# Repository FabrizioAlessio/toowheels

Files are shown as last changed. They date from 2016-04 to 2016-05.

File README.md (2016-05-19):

# toowheels
TooWheels is a DIY wheelchair for people with disability. I'ts a patent pending project of Fabrizio Alessio, released in open source version (CC licence non commercial,share alike international 4.0) to be usefull for people all over the world.

For any information see our website www.toowheels.org, our Facebook page "toowheels" or feel free to contact by mail at: alessiofabriziogiorgio@gmail.com

I'ts an evolving project of Fabrizio Alessio started in FabLabTorino, selected in 2014 as one of the 30 best project in the world at the "Global Fab Awards" and winner of the italian prize "Compasso d'Oro - Targa Giovani" at the XXIV edition of the ADI DESIGN INDEX. 

We are developing a lots of projects all around the world, involving FabLabs, Associations, Designers and Research groups. Contact us and join TooWheels project!

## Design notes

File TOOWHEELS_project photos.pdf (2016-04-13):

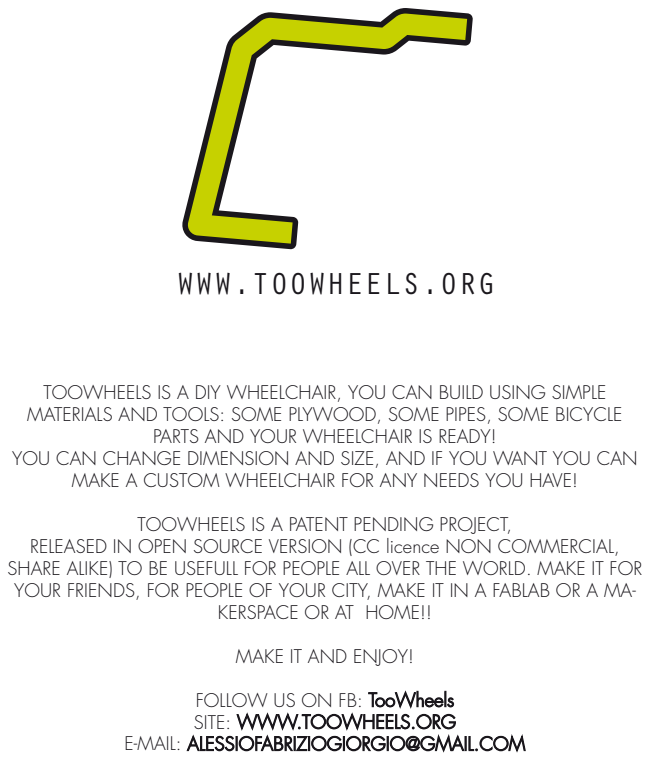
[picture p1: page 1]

WWW.TOOWHEELS.ORG

TOOWHEELS IS A DIY WHEELCHAIR, YOU CAN BUILD USING SIMPLE
MATERIALS AND TOOLS: SOME PLYWOOD, SOME PIPES, SOME BICYCLE
YOU CAN CHANGE DIMENSION AND SIZE, AND IF YOU WANT YOU CAN
MAKE A CUSTOM WHEELCHAIR FOR ANY NEEDS YOU HAVE!
TOOWHEELS IS A PATENT PENDING PROJECT,

PARTS AND YOUR WHEELCHAIR IS READY!

RELEASED IN OPEN SOURCE VERSION (CC licence NON COMMERCIAL,
SHARE ALIKE) TO BE USEFULL FOR PEOPLE ALL OVER THE WORLD. MAKE IT FOR
YOUR FRIENDS, FOR PEOPLE OF YOUR CITY, MAKE IT IN A FABLAB OR A MA-

KERSPACE OR AT HOME!!
MAKE IT AND ENJOY!
FOLLOW US ON FB: TooWheels
SITE: WWW.TOOWHEELS.ORG
E-MAIL: ALESSIOFABRIZIOGIORGIO@GMAIL.COM

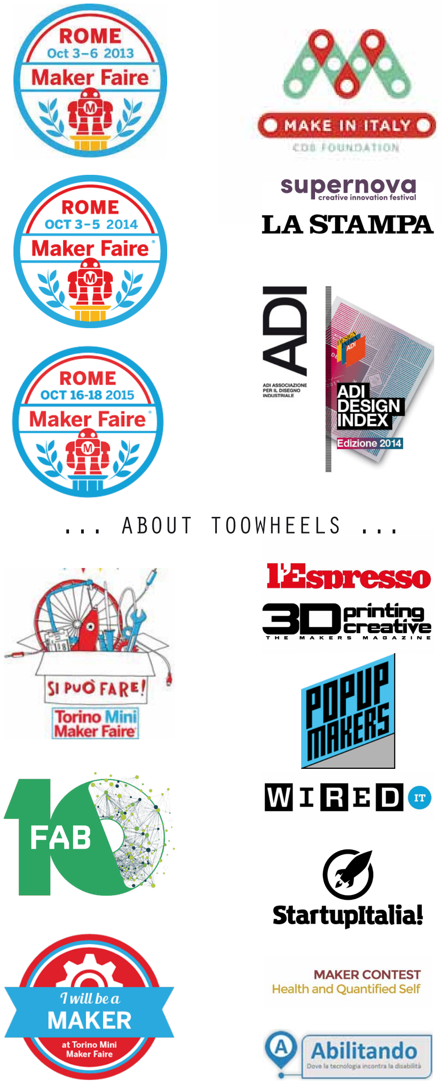
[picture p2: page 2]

... ABOUT TOOWHEELS ...

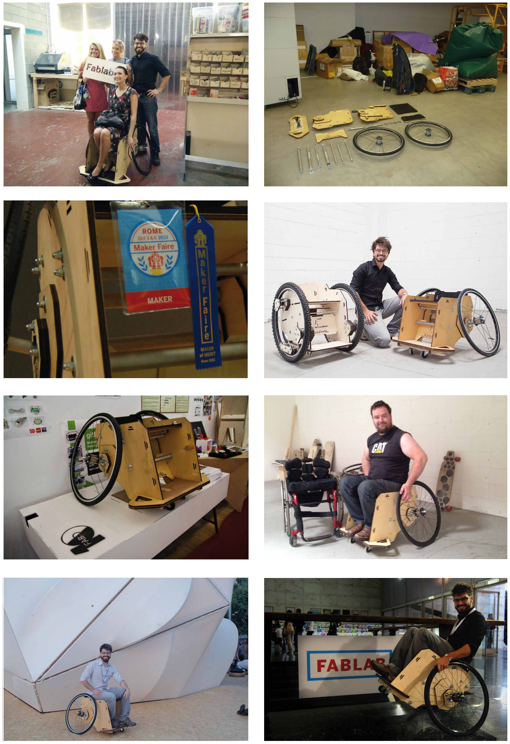
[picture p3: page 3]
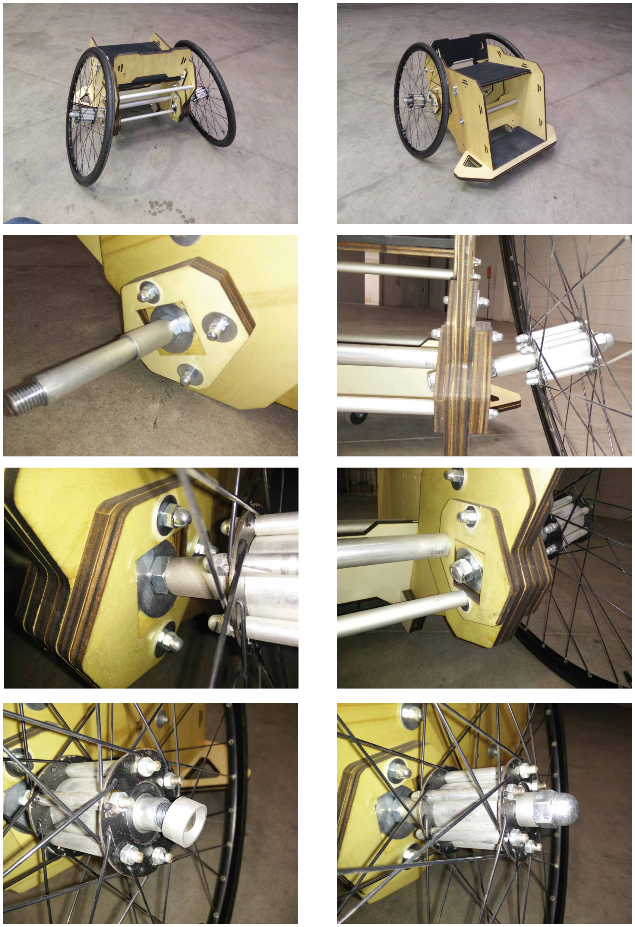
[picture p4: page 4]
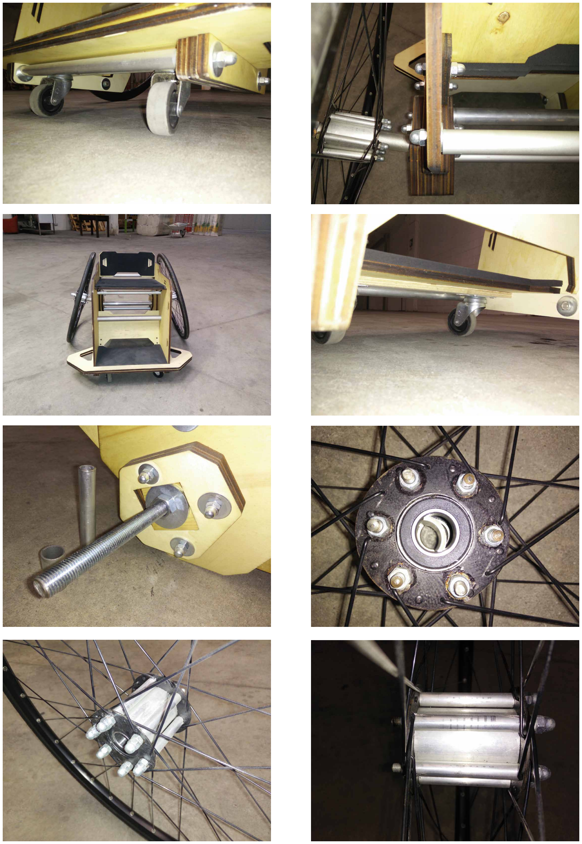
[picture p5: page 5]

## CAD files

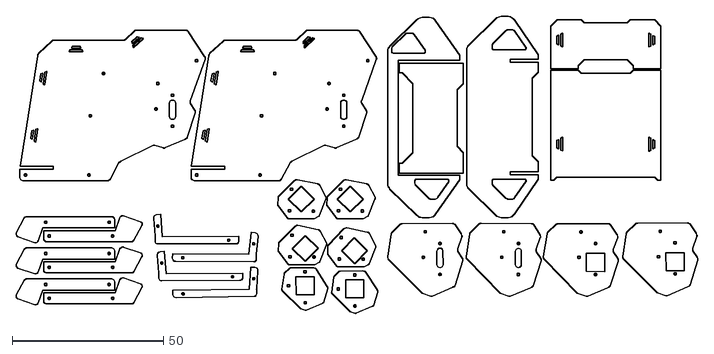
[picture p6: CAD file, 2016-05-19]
TOOWHEELS_2D PLANS.dxf
225.4 x 98.2

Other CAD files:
TOOWHEELS_2D PLANS.dwg

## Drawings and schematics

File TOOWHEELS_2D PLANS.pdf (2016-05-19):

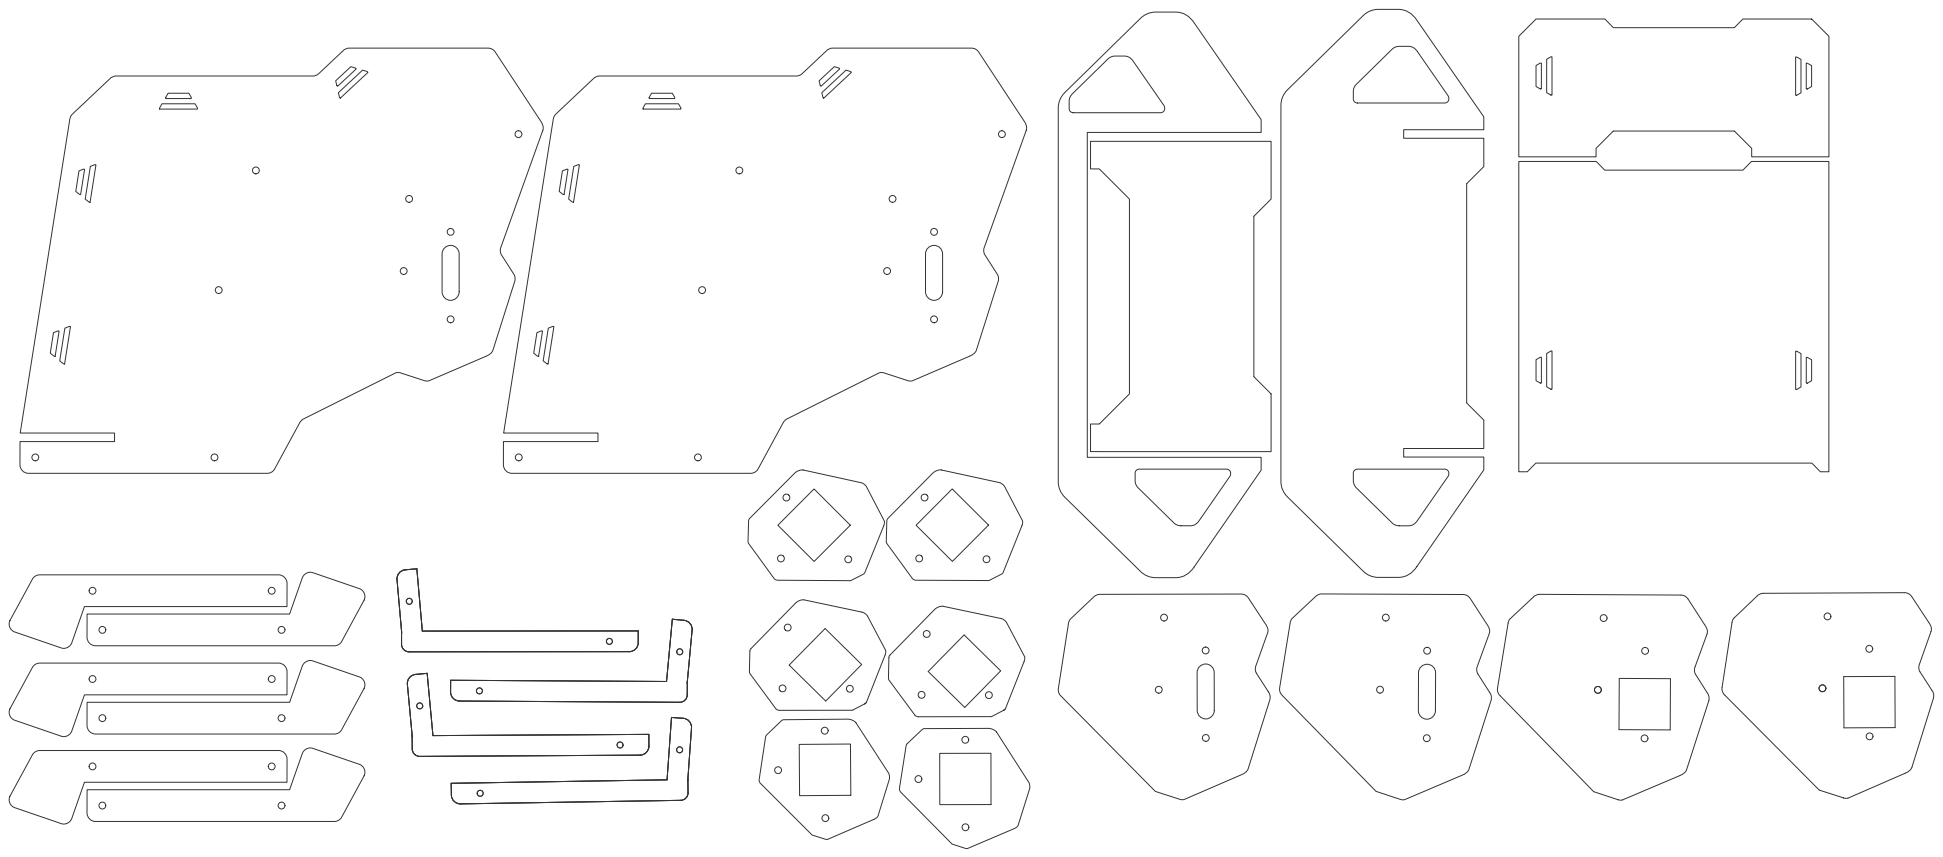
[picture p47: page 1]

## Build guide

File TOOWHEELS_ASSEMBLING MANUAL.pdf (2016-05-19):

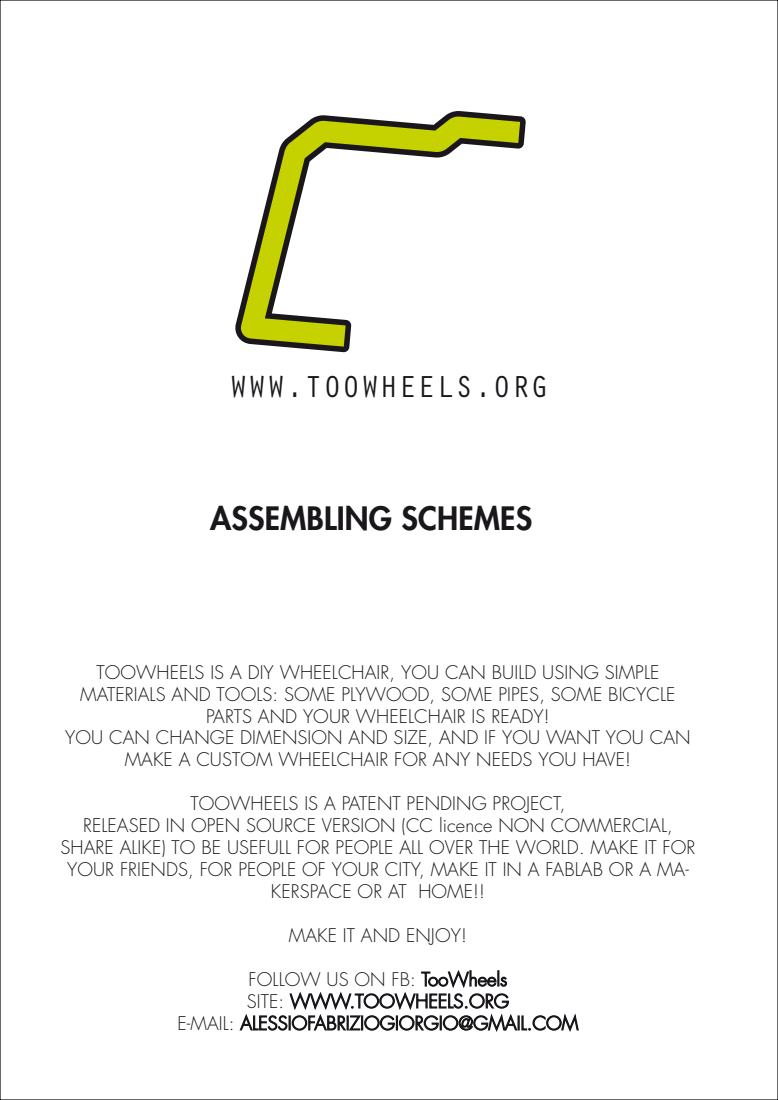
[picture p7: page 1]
ASSEMBLING SCHEMES

WWW.TOOWHEELS.ORG

TOOWHEELS IS A DIY WHEELCHAIR, YOU CAN BUILD USING SIMPLE
MATERIALS AND TOOLS: SOME PLYWOOD, SOME PIPES, SOME BICYCLE
YOU CAN CHANGE DIMENSION AND SIZE, AND IF YOU WANT YOU CAN
MAKE A CUSTOM WHEELCHAIR FOR ANY NEEDS YOU HAVE!
TOOWHEELS IS A PATENT PENDING PROJECT,

PARTS AND YOUR WHEELCHAIR IS READY!

RELEASED IN OPEN SOURCE VERSION (CC licence NON COMMERCIAL,
SHARE ALIKE) TO BE USEFULL FOR PEOPLE ALL OVER THE WORLD. MAKE IT FOR
YOUR FRIENDS, FOR PEOPLE OF YOUR CITY, MAKE IT IN A FABLAB OR A MA-

KERSPACE OR AT HOME!!
MAKE IT AND ENJOY!
FOLLOW US ON FB: TooWheels
SITE: WWW.TOOWHEELS.ORG
E-MAIL: ALESSIOFABRIZIOGIORGIO@GMAIL.COM

## POSIZIONA LA SEDUTA

1

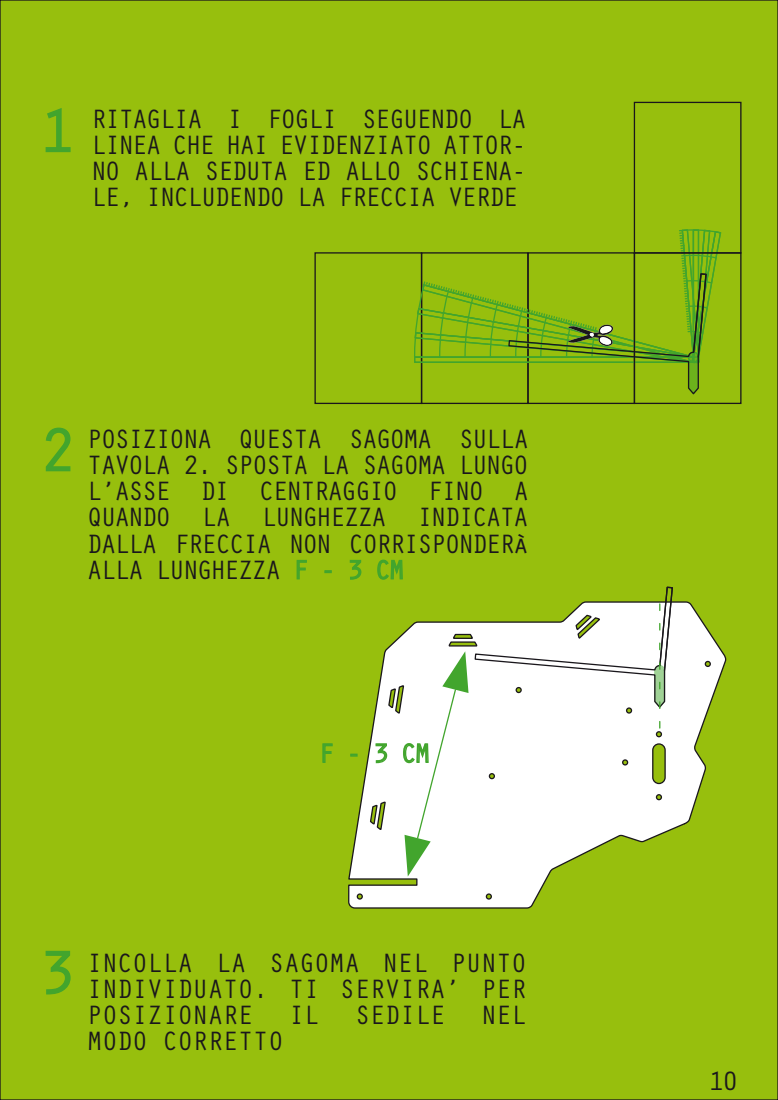
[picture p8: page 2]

RITAGLIA I FOGLI SEGUENDO LA
LINEA CHE HAI EVIDENZIATO ATTOR- NO ALLA SEDUTA ED ALLO SCHIENA- LE, INCLUDENDO LA FRECCIA VERDE

POSIZIONA QUESTA SAGOMA SULLA
TAVOLA 2. SPOSTA LA SAGOMA LUNGO
L’ASSE DI CENTRAGGIO FINO A
QUANDO LA LUNGHEZZA INDICATA
DALLA FRECCIA NON CORRISPONDERà
ALLA LUNGHEZZA F - 3 CM

INCOLLA LA SAGOMA NEL PUNTO
INDIVIDUATO. TI SERVIRA’ PER
POSIZIONARE IL SEDILE NEL
MODO CORRETTO

## BACKREST,SEAT,BUMPER SUPPORT

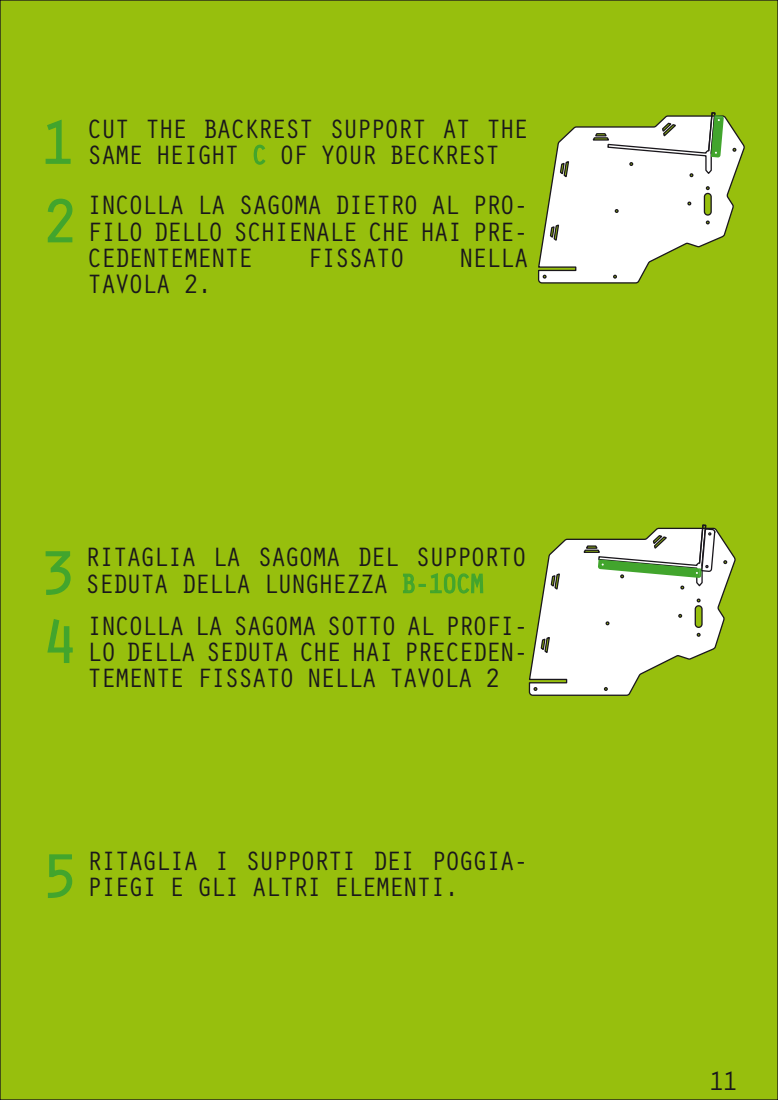
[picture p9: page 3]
2INCOLLA LA SAGOMA DIETRO AL PRO- FILO DELLO SCHIENALE CHE HAI PRE- CEDENTEMENTE; FISSATO; NELLA; TAVOLA 2.

1 CUT THE BACKREST SUPPORT AT THE
SAME HEIGHT C OF YOUR BECKREST

3RITAGLIA LA SAGOMA DEL SUPPORTO
SEDUTA DELLA LUNGHEZZA B-10CM
4INCOLLA LA SAGOMA SOTTO AL PROFI- LO DELLA SEDUTA CHE HAI PRECEDEN- TEMENTE FISSATO NELLA TAVOLA 2

5RITAGLIA I SUPPORTI DEI POGGIA- PIEGI E GLI ALTRI ELEMENTI.

ASSEMBLAGGIO | FASE11

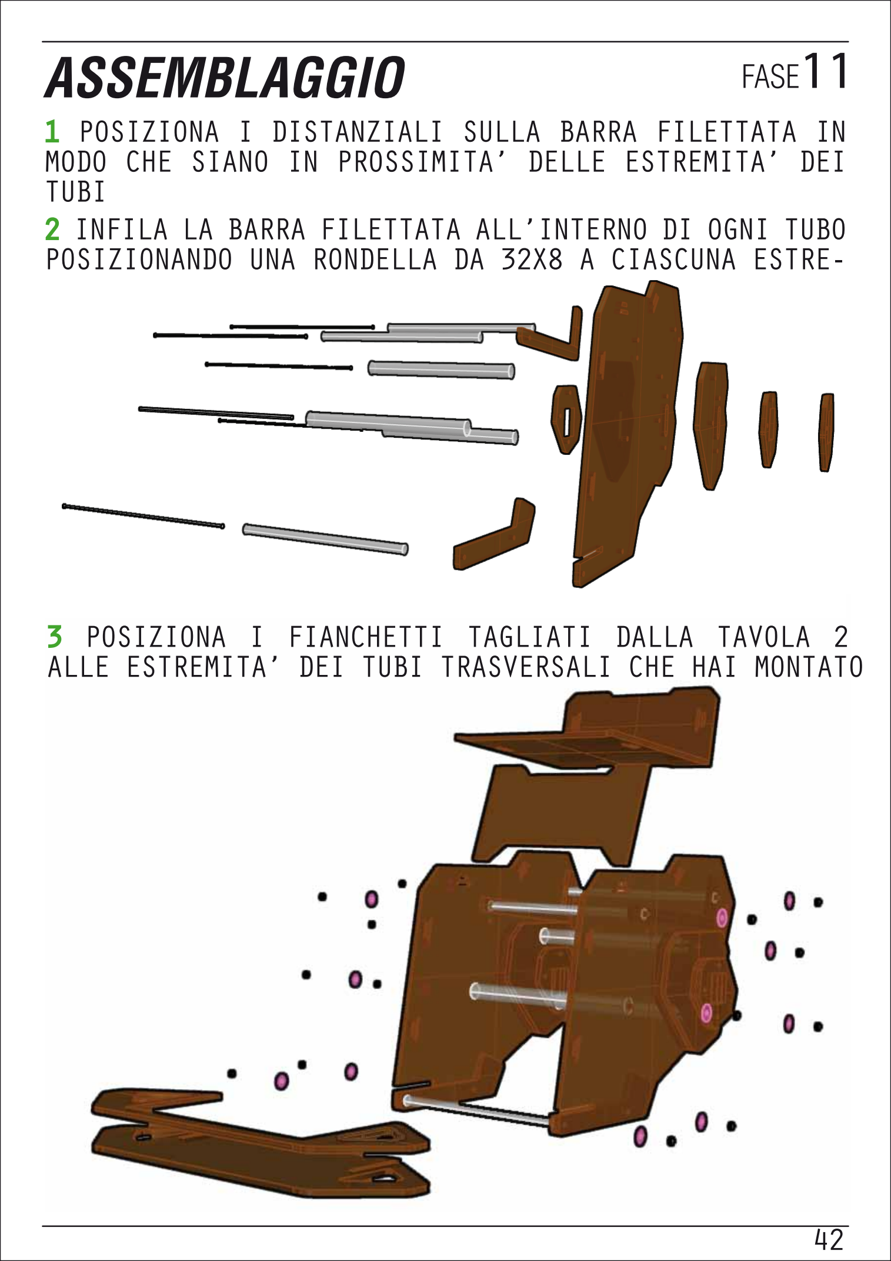
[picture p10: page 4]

1 POSIZIONA I DISTANZIALI SULLA BARRA FILETTATA IN MODO CHE SIANO IN PROSSIMITA’ DELLE ESTREMITA’ DEI TUBI
2 INFILA LA BARRA FILETTATA ALL’INTERNO DI OGNI TUBO POSIZIONANDO UNA RONDELLA DA 32X8 A CIASCUNA ESTRE- MITA’

3 POSIZIONA I FIANCHETTI TAGLIATI DALLA TAVOLA 2 ALLE ESTREMITA’ DEI TUBI TRASVERSALI CHE HAI MONTATO

## PIPES AND RODS

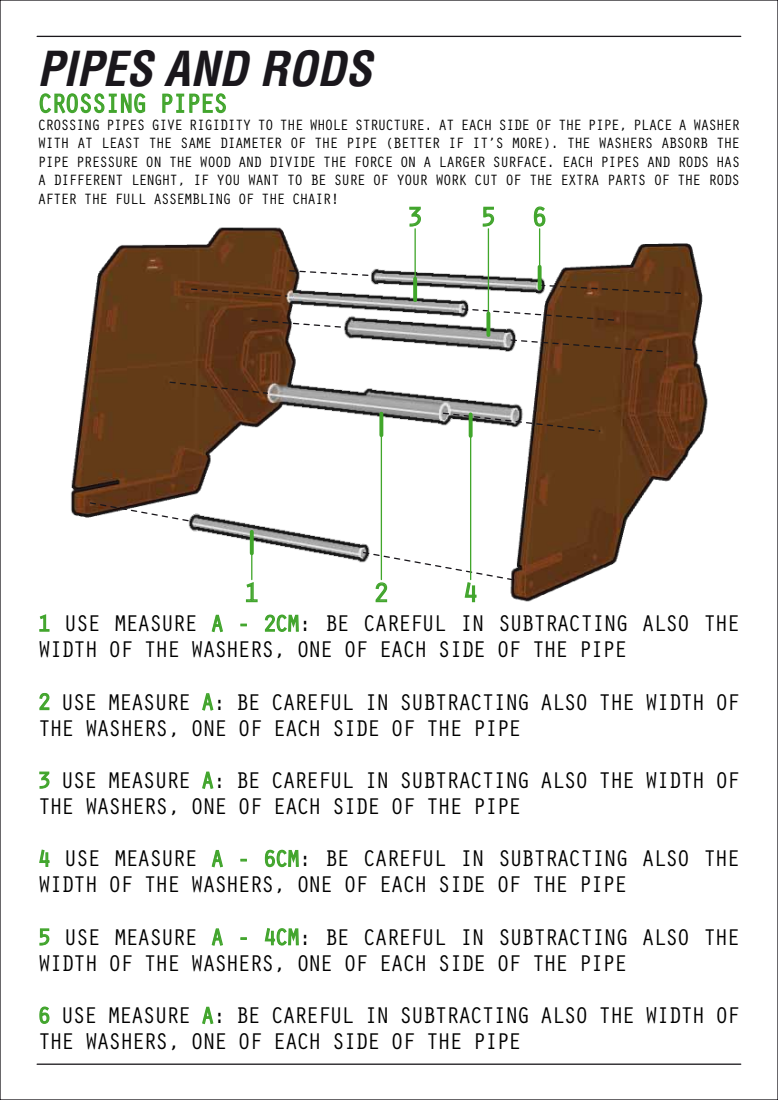
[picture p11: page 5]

CROSSING PIPES
CROSSING PIPES GIVE RIGIDITY TO THE WHOLE STRUCTURE. AT EACH SIDE OF THE PIPE, PLACE A WASHER
WITH AT LEAST THE SAME DIAMETER OF THE PIPE (BETTER IF IT’S MORE). THE WASHERS ABSORB THE
PIPE PRESSURE ON THE WOOD AND DIVIDE THE FORCE ON A LARGER SURFACE. EACH PIPES AND RODS HAS
A DIFFERENT LENGHT, IF YOU WANT TO BE SURE OF YOUR WORK CUT OF THE EXTRA PARTS OF THE RODS
AFTER THE FULL ASSEMBLING OF THE CHAIR!

1 USE MEASURE A - 2CM: BE CAREFUL IN SUBTRACTING ALSO THE
WIDTH OF THE WASHERS, ONE OF EACH SIDE OF THE PIPE
2 USE MEASURE A: BE CAREFUL IN SUBTRACTING ALSO THE WIDTH OF
THE WASHERS, ONE OF EACH SIDE OF THE PIPE
3 USE MEASURE A: BE CAREFUL IN SUBTRACTING ALSO THE WIDTH OF
4 USE MEASURE A - 6CM: BE CAREFUL IN SUBTRACTING ALSO THE
5 USE MEASURE A - 4CM: BE CAREFUL IN SUBTRACTING ALSO THE
6 USE MEASURE A: BE CAREFUL IN SUBTRACTING ALSO THE WIDTH OF

## HUB

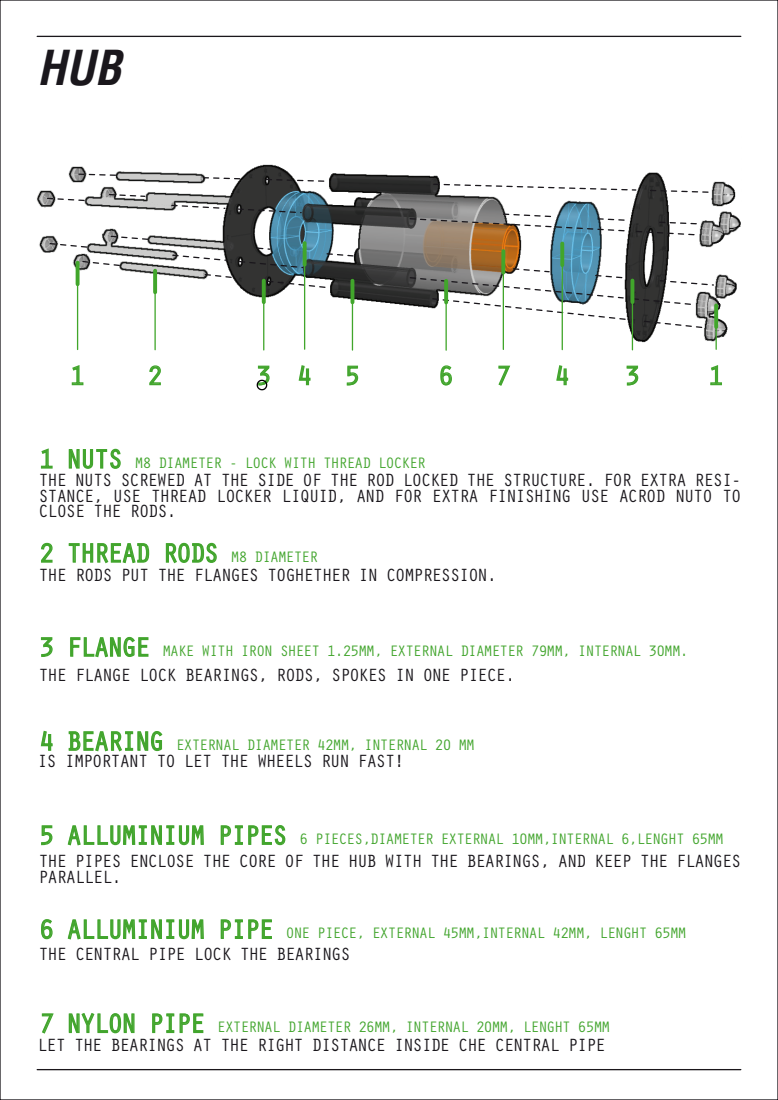
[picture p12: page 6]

1 NUTS M8 DIAMETER - LOCK WITH THREAD LOCKER
THE NUTS SCREWED AT THE SIDE OF THE ROD LOCKED THE STRUCTURE. FOR EXTRA RESI- STANCE, USE THREAD LOCKER LIQUID, AND FOR EXTRA FINISHING USE ACROD NUTO TO
CLOSE THE RODS.
2 THREAD RODS M8 DIAMETER
THE RODS PUT THE FLANGES TOGHETHER IN COMPRESSION.

3 FLANGE MAKE WITH IRON SHEET 1.25MM, EXTERNAL DIAMETER 79MM, INTERNAL 30MM.
THE FLANGE LOCK BEARINGS, RODS, SPOKES IN ONE PIECE.

4 BEARING EXTERNAL DIAMETER 42MM, INTERNAL 20 MM
IS IMPORTANT TO LET THE WHEELS RUN FAST!

5 ALLUMINIUM PIPES 6 PIECES,DIAMETER EXTERNAL 10MM,INTERNAL 6,LENGHT 65MM
THE PIPES ENCLOSE THE CORE OF THE HUB WITH THE BEARINGS, AND KEEP THE FLANGES
PARALLEL.

6 ALLUMINIUM PIPE ONE PIECE, EXTERNAL 45MM,INTERNAL 42MM, LENGHT 65MM
THE CENTRAL PIPE LOCK THE BEARINGS

7 NYLON PIPE EXTERNAL DIAMETER 26MM, INTERNAL 20MM, LENGHT 65MM
LET THE BEARINGS AT THE RIGHT DISTANCE INSIDE CHE CENTRAL PIPE

## AXLE

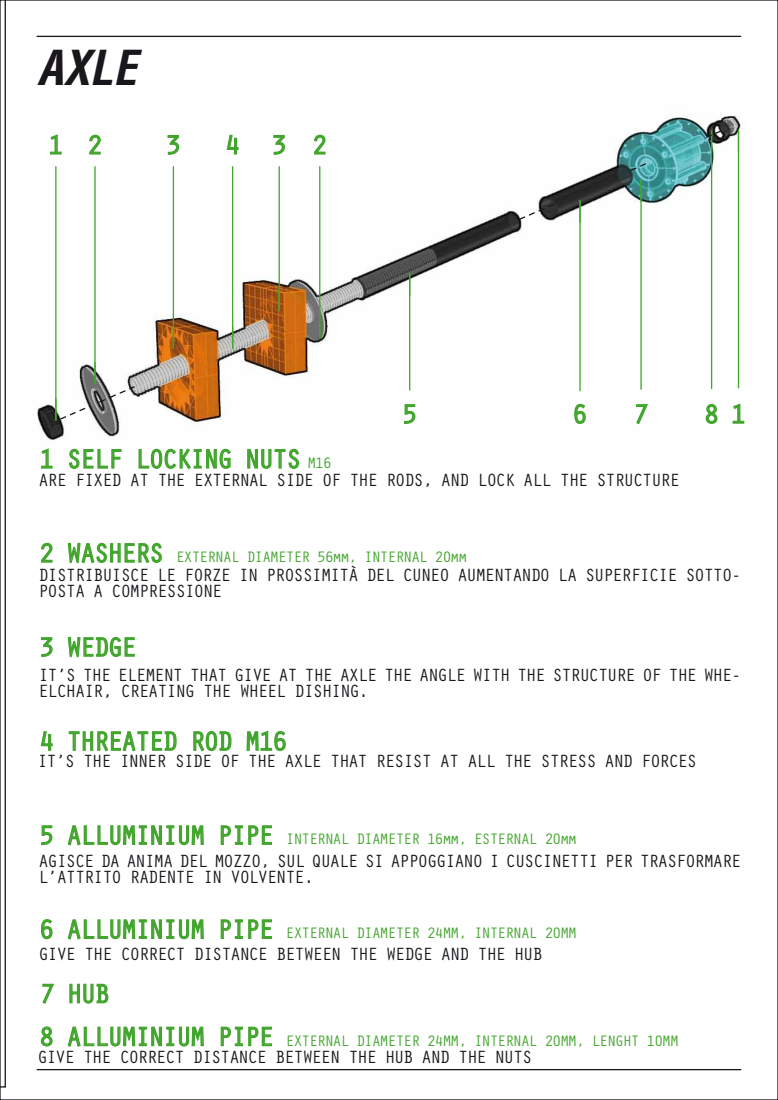
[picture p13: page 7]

1 SELF LOCKING NUTS M16
ARE FIXED AT THE EXTERNAL SIDE OF THE RODS, AND LOCK ALL THE STRUCTURE

2 WASHERS EXTERNAL DIAMETER 56mm, INTERNAL 20mm
DISTRIBUISCE LE FORZE IN PROSSIMITÀ DEL CUNEO AUMENTANDO LA SUPERFICIE SOTTO- POSTA A COMPRESSIONE
3 WEDGE
IT’S THE ELEMENT THAT GIVE AT THE AXLE THE ANGLE WITH THE STRUCTURE OF THE WHE- ELCHAIR, CREATING THE WHEEL DISHING.
4 THREATED ROD M16
IT’S THE INNER SIDE OF THE AXLE THAT RESIST AT ALL THE STRESS AND FORCES

5 ALLUMINIUM PIPE INTERNAL DIAMETER 16mm, ESTERNAL 20mm
AGISCE DA ANIMA DEL MOZZO, SUL QUALE SI APPOGGIANO I CUSCINETTI PER TRASFORMARE
L’ATTRITO RADENTE IN VOLVENTE.

6 ALLUMINIUM PIPE EXTERNAL DIAMETER 24MM, INTERNAL 20MM
GIVE THE CORRECT DISTANCE BETWEEN THE WEDGE AND THE HUB
7 HUB

8 ALLUMINIUM PIPE EXTERNAL DIAMETER 24MM, INTERNAL 20MM, LENGHT 10MM
GIVE THE CORRECT DISTANCE BETWEEN THE HUB AND THE NUTS

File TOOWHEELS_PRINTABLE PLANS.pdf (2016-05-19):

WWW.TOOWHEELS.ORG

SIZE-ME: ERGONOMICAL DIMENSION

TOOWHEELS IS A DIY WHEELCHAIR, YOU CAN BUILD USING SIMPLE
MATERIALS AND TOOLS: SOME PLYWOOD, SOME PIPES, SOME BICYCLE
YOU CAN CHANGE DIMENSION AND SIZE, AND IF YOU WANT YOU CAN
MAKE A CUSTOM WHEELCHAIR FOR ANY NEEDS YOU HAVE!
TOOWHEELS IS A PATENT PENDING PROJECT,

PARTS AND YOUR WHEELCHAIR IS READY!

RELEASED IN OPEN SOURCE VERSION (CC licence NON COMMERCIAL,
SHARE ALIKE) TO BE USEFULL FOR PEOPLE ALL OVER THE WORLD. MAKE IT FOR
YOUR FRIENDS, FOR PEOPLE OF YOUR CITY, MAKE IT IN A FABLAB OR A MA-

KERSPACE OR AT HOME!!
MAKE IT AND ENJOY!
FOLLOW US ON FB: TooWheels
SITE: WWW.TOOWHEELS.ORG
E-MAIL: ALESSIOFABRIZIOGIORGIO@GMAIL.COM

## CREATE THE PLANS! PLANS 1

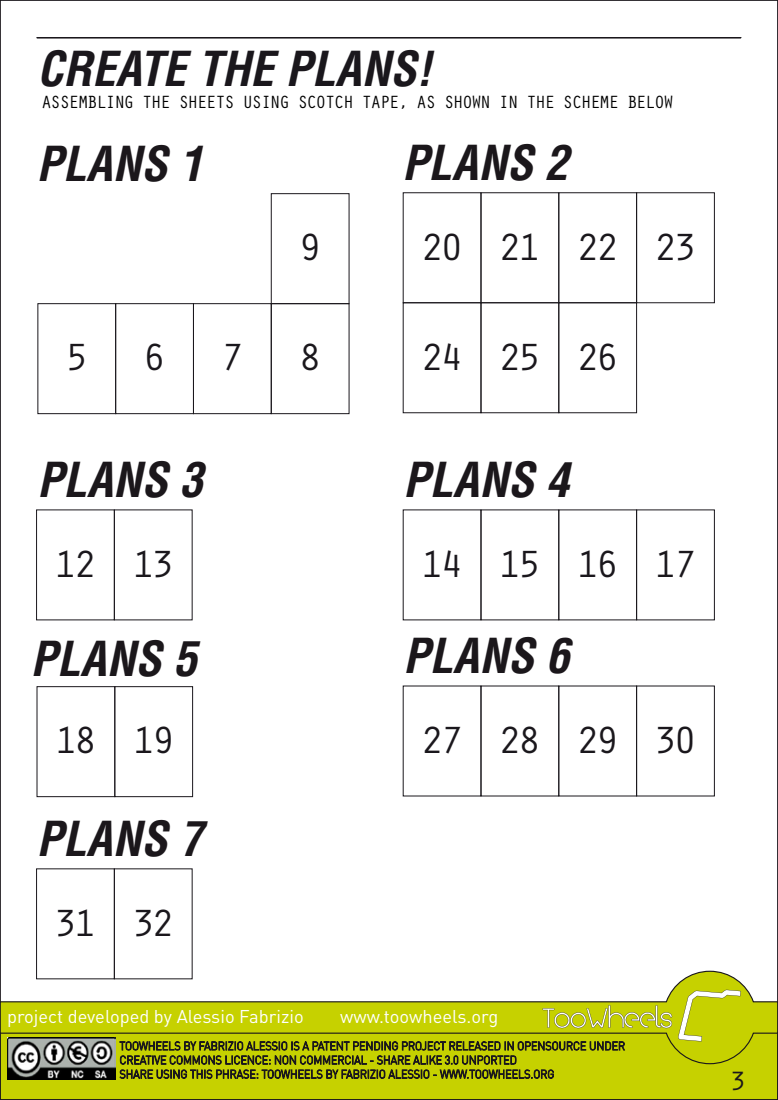
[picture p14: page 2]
project developed by Alessio Fabrizio; www.toowheels.org; PLANS 2; PLANS 3; PLANS 4; PLANS 5; PLANS 6; PLANS 7

ASSEMBLING THE SHEETS USING SCOTCH TAPE, AS SHOWN IN THE SCHEME BELOW

TOOWHEELS BY FABRIZIO ALESSIO IS A PATENT PENDING PROJECT RELEASED IN OPENSOURCE UNDER
CREATIVE COMMONS LICENCE: NON COMMERCIAL - SHARE ALIKE 3.0 UNPORTED
SHARE USING THIS PHRASE: TOOWHEELS BY FABRIZIO ALESSIO - WWW.TOOWHEELS.ORG

## SIZE-ME!

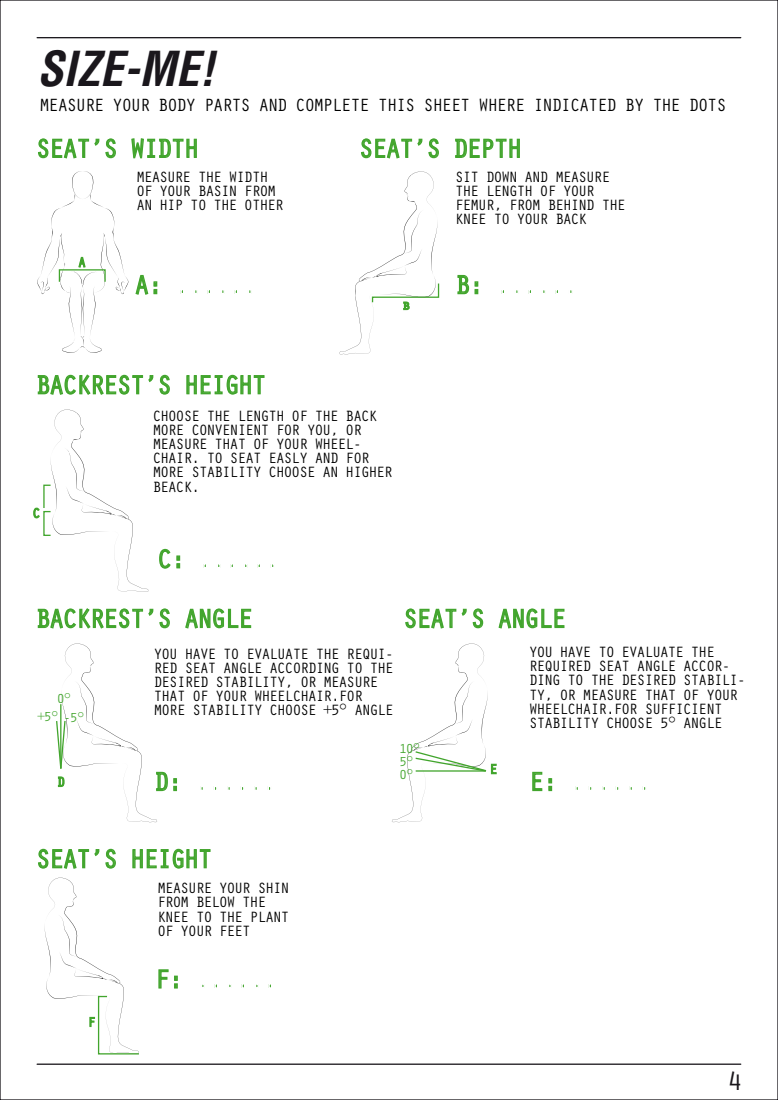
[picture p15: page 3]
BACKREST’S HEIGHT; BACKREST’S ANGLE; SEAT’S HEIGHT; SEAT’S DEPTH; SEAT’S ANGLE

MEASURE YOUR BODY PARTS AND COMPLETE THIS SHEET WHERE INDICATED BY THE DOTS
SEAT’S WIDTH

MEASURE THE WIDTH
OF YOUR BASIN FROM
AN HIP TO THE OTHER

SIT DOWN AND MEASURE
THE LENGTH OF YOUR
FEMUR, FROM BEHIND THE
KNEE TO YOUR BACK

CHOOSE THE LENGTH OF THE BACK
MORE CONVENIENT FOR YOU, OR
MEASURE THAT OF YOUR WHEEL- CHAIR. TO SEAT EASLY AND FOR
MORE STABILITY CHOOSE AN HIGHER
BEACK.

YOU HAVE TO EVALUATE THE REQUI- RED SEAT ANGLE ACCORDING TO THE
DESIRED STABILITY, OR MEASURE
THAT OF YOUR WHEELCHAIR.FOR
MORE STABILITY CHOOSE +5° ANGLE

YOU HAVE TO EVALUATE THE
REQUIRED SEAT ANGLE ACCOR- DING TO THE DESIRED STABILI- TY, OR MEASURE THAT OF YOUR

WHEELCHAIR.FOR SUFFICIENT
STABILITY CHOOSE 5° ANGLE

MEASURE YOUR SHIN
FROM BELOW THE
KNEE TO THE PLANT
OF YOUR FEET

## SEAT-TIME!

15°

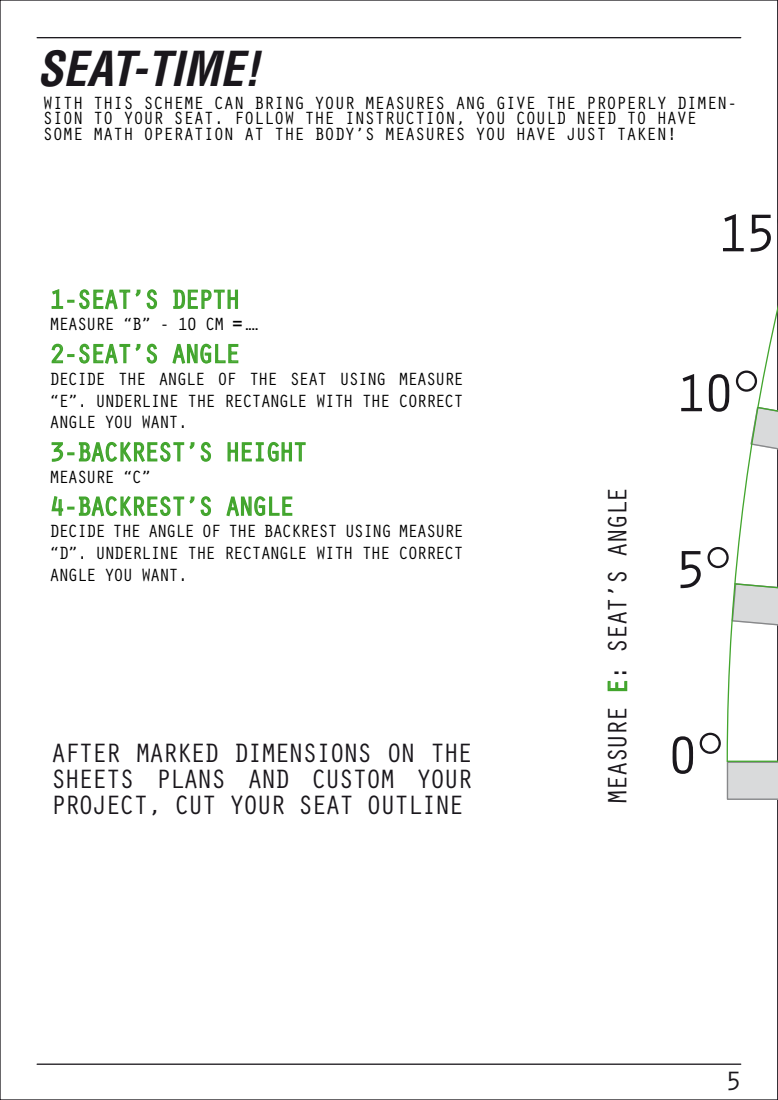
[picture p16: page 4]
MEASURE; E: SEAT’S ANGLE

WITH THIS SCHEME CAN BRING YOUR MEASURES ANG GIVE THE PROPERLY DIMEN- SION TO YOUR SEAT. FOLLOW THE INSTRUCTION, YOU COULD NEED TO HAVE
SOME MATH OPERATION AT THE BODY’S MEASURES YOU HAVE JUST TAKEN!

1-SEAT’S DEPTH
MEASURE “B” - 10 CM = ....
2-SEAT’S ANGLE
DECIDE THE ANGLE OF THE SEAT USING MEASURE
“E”. UNDERLINE THE RECTANGLE WITH THE CORRECT
ANGLE YOU WANT.
3-BACKREST’S HEIGHT
MEASURE “C”
4-BACKREST’S ANGLE
DECIDE THE ANGLE OF THE BACKREST USING MEASURE
“D”. UNDERLINE THE RECTANGLE WITH THE CORRECT

AFTER MARKED DIMENSIONS ON THE
SHEETS PLANS AND CUSTOM YOUR
PROJECT, CUT YOUR SEAT OUTLINE

15°
45cm

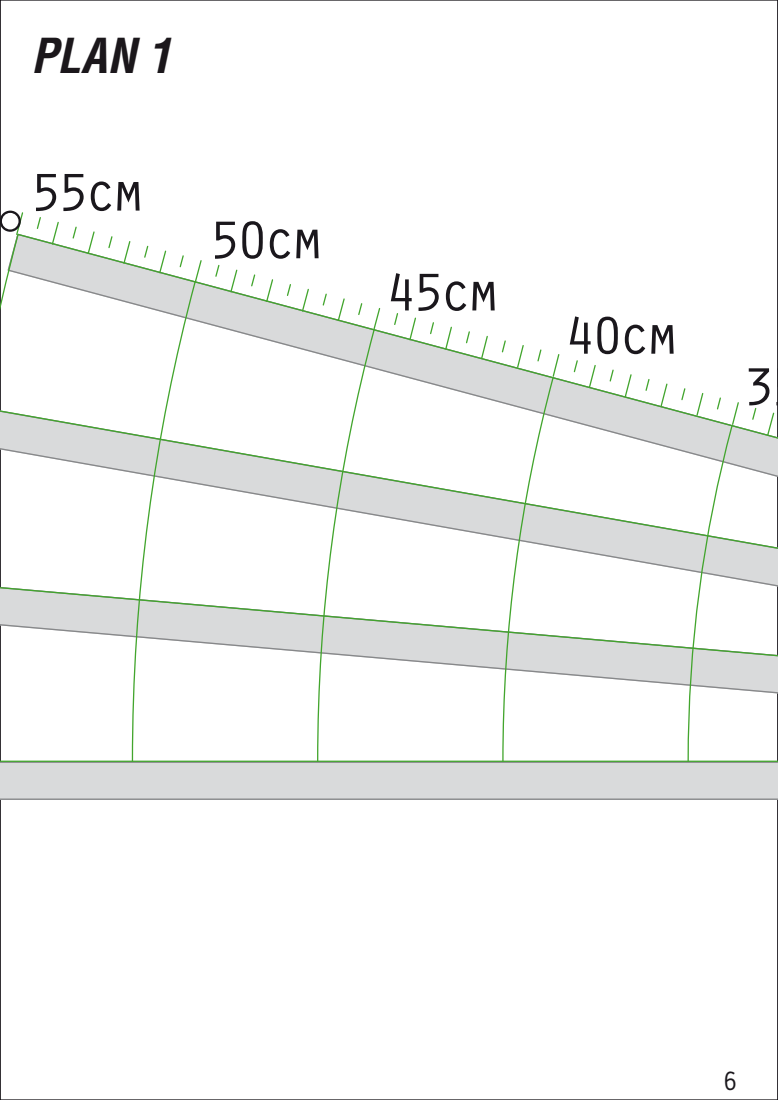
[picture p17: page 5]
PLAN 1

## PLAN 1

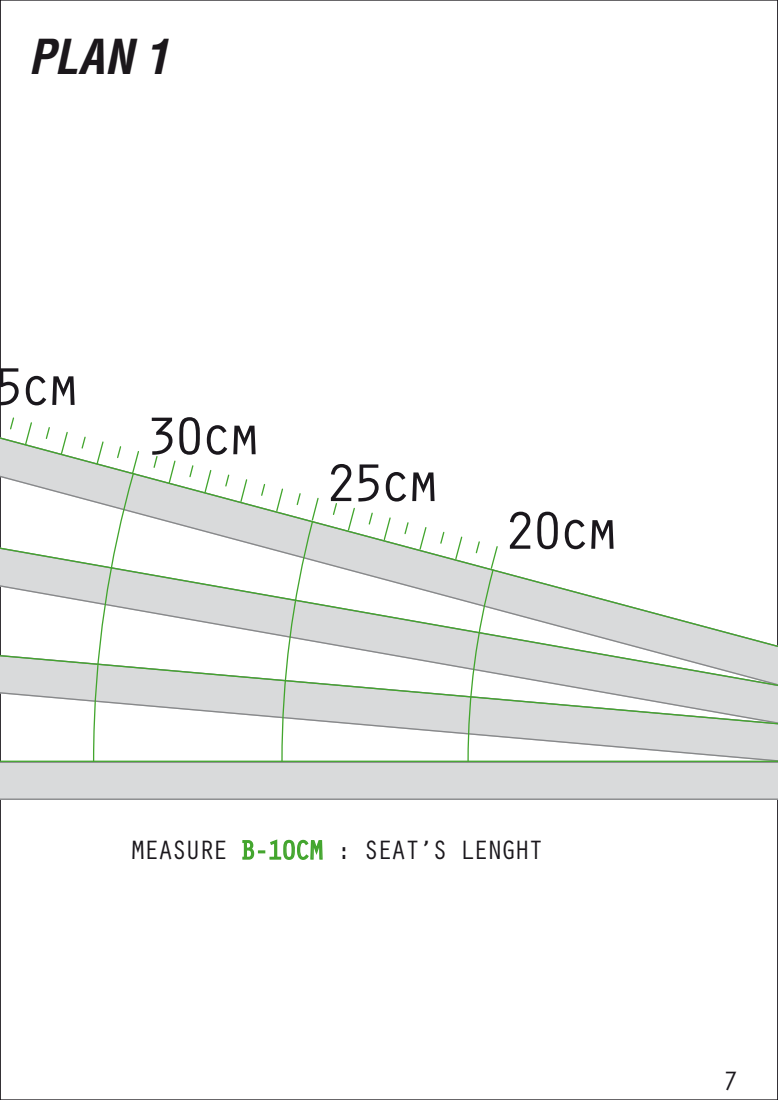
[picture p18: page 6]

MEASURE B-10CM : SEAT’S LENGHT

15cm

20cm

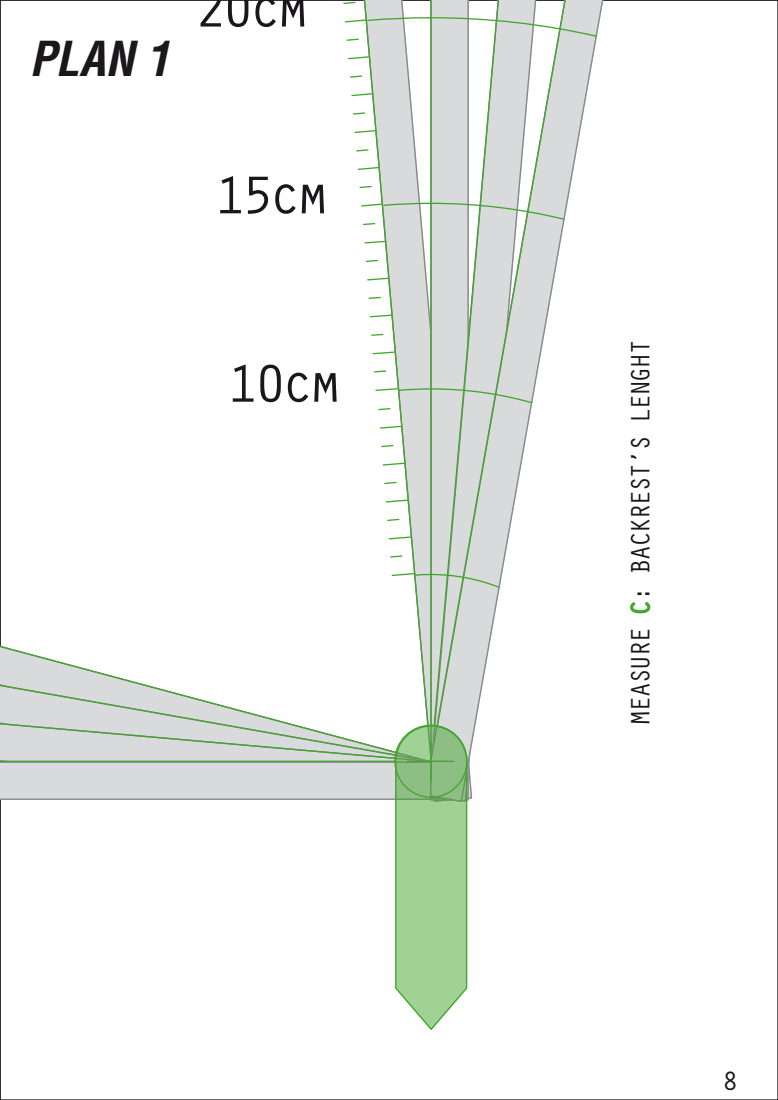
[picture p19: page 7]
PLAN 1

MEASURE C: BACKREST’S LENGHT

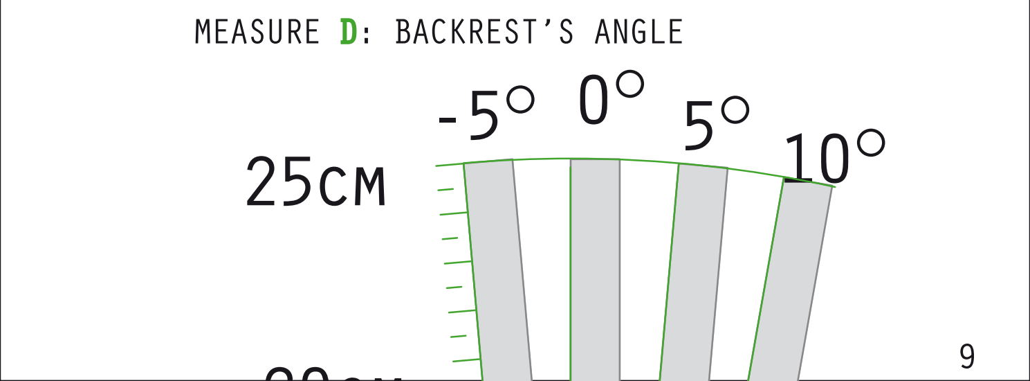
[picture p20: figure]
MEASURE D: BACKREST’S ANGLE

20cm

## PLAN 1

## PLAN 3

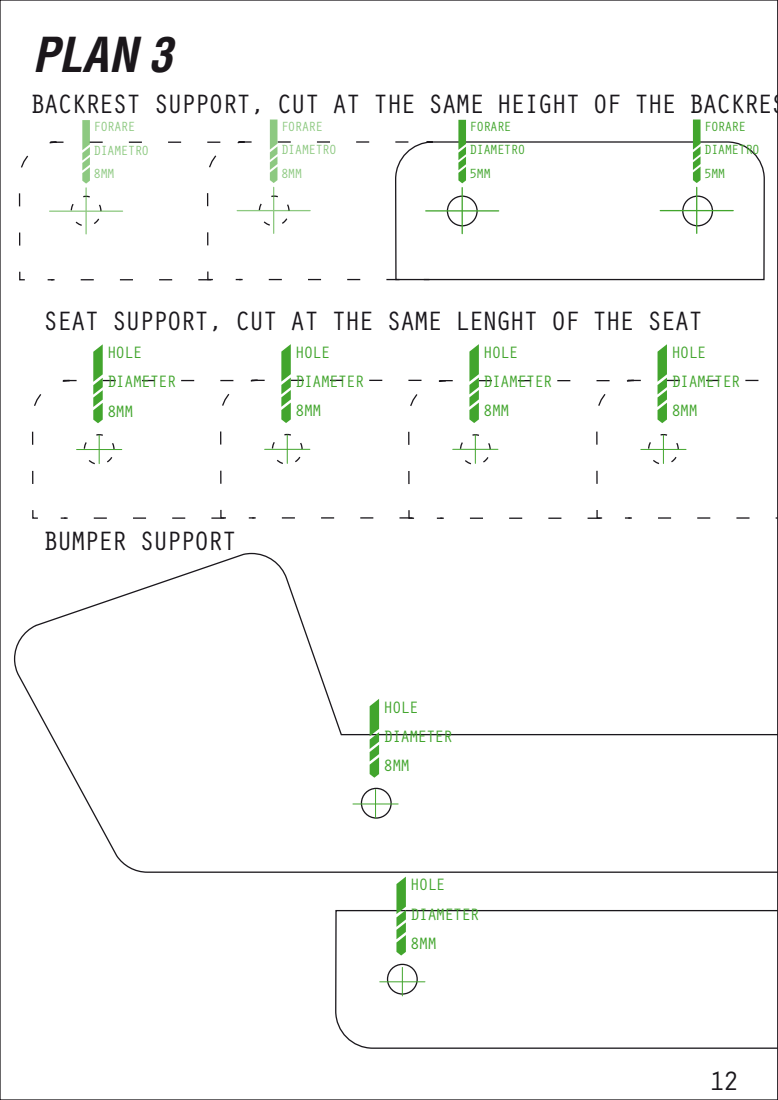
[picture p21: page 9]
BUMPER SUPPORT; FORARE DIAMETRO 5MM; FORARE DIAMETRO 8MM; HOLE DIAMETER 8MM

BACKREST SUPPORT, CUT AT THE SAME HEIGHT OF THE BACKREST

SEAT SUPPORT, CUT AT THE SAME LENGHT OF THE SEAT
HOLE
DIAMETER

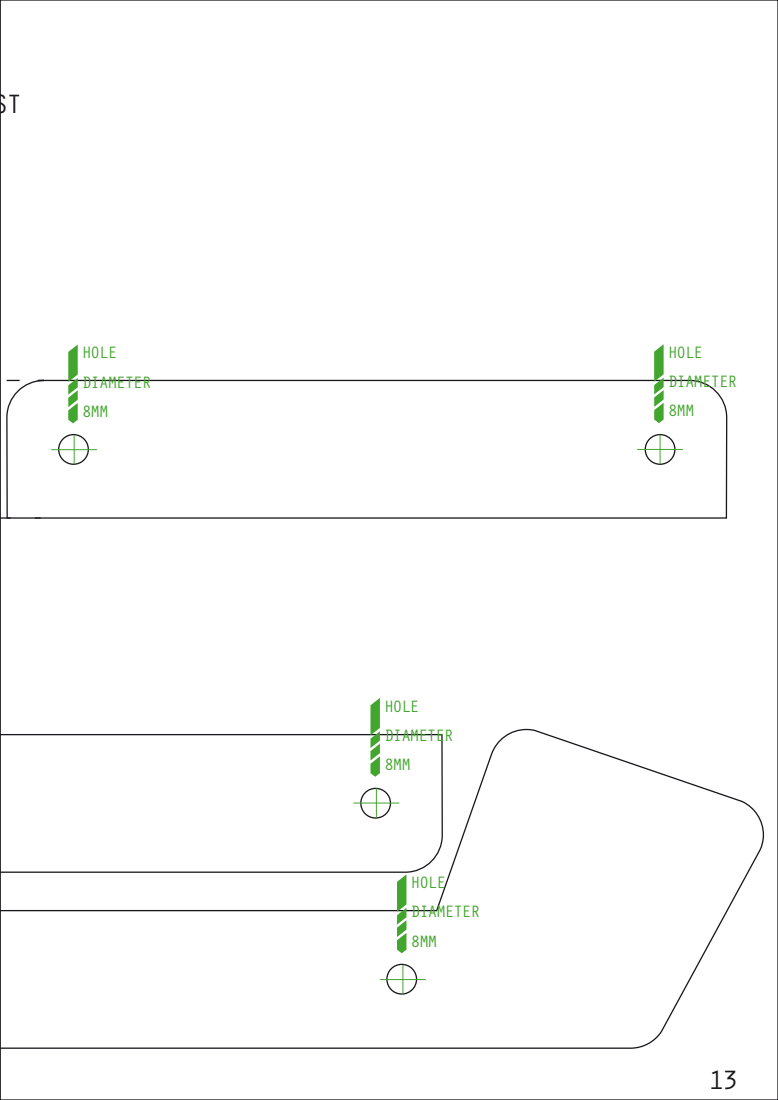
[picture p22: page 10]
HOLE DIAMETER 8MM

BACKREST SUPPORT, CUT AT THE SAME HEIGHT OF THE BACKREST

## PLAN 4

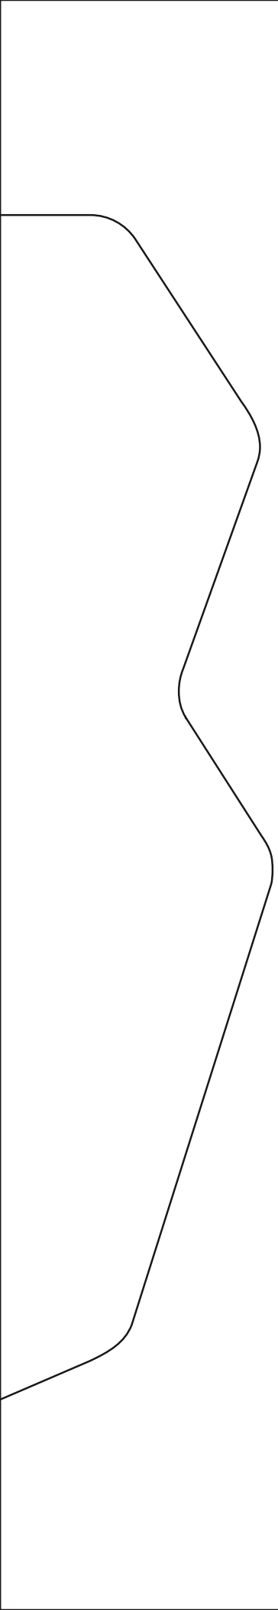
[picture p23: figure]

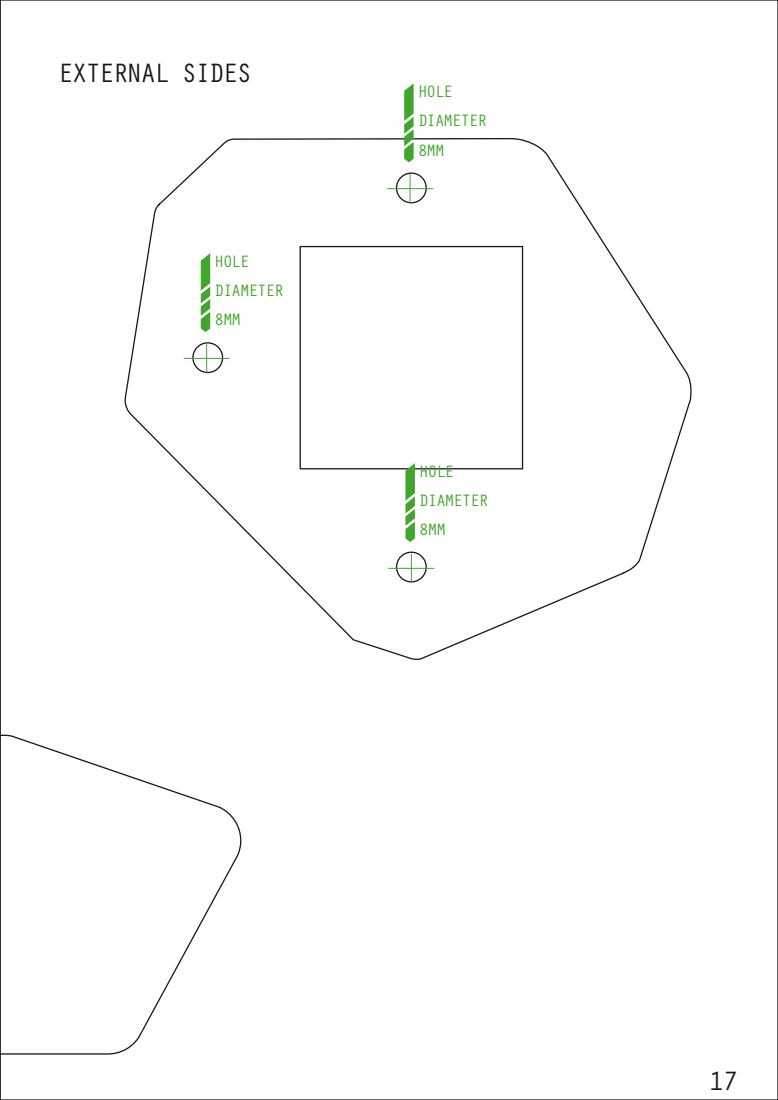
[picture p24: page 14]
HOLE DIAMETER 8MM; EXTERNAL SIDES

## PLAN 5

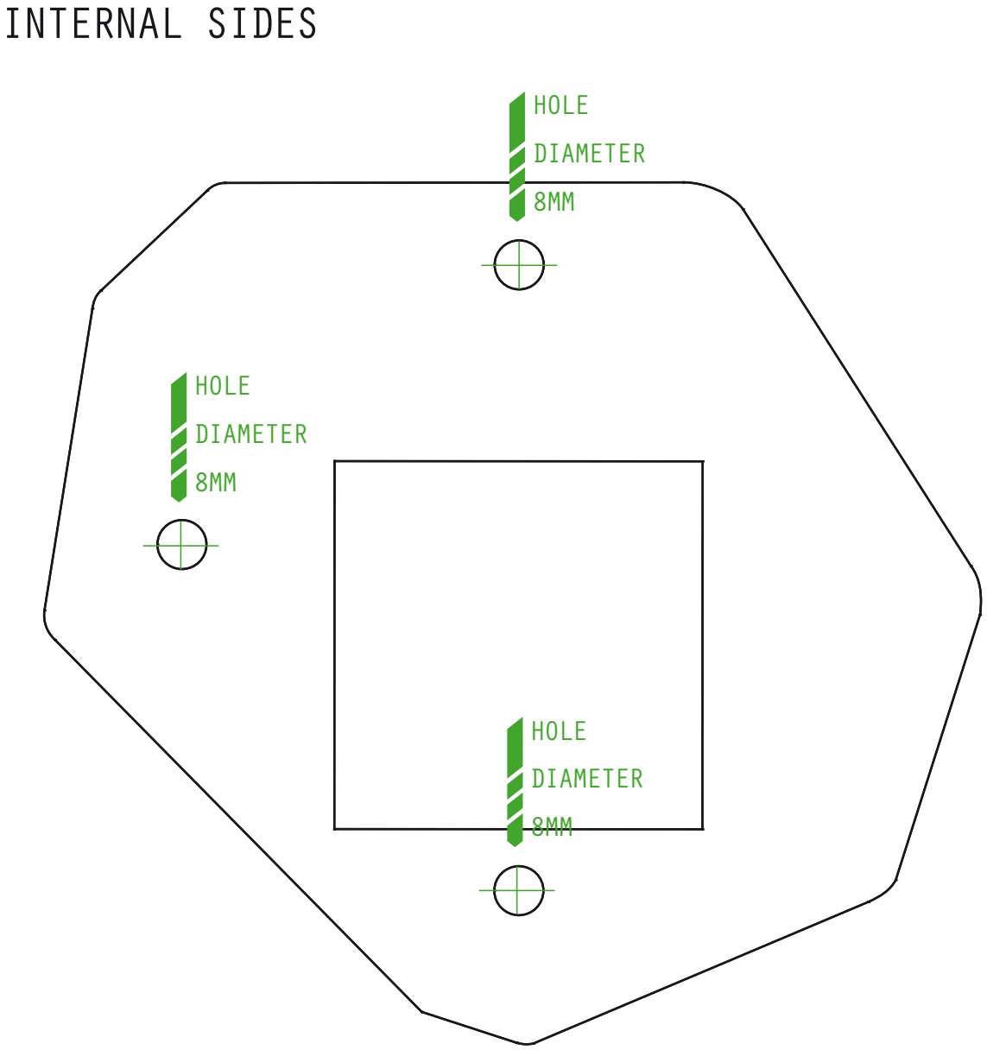
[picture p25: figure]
HOLE DIAMETER 8MM; INTERNAL SIDES

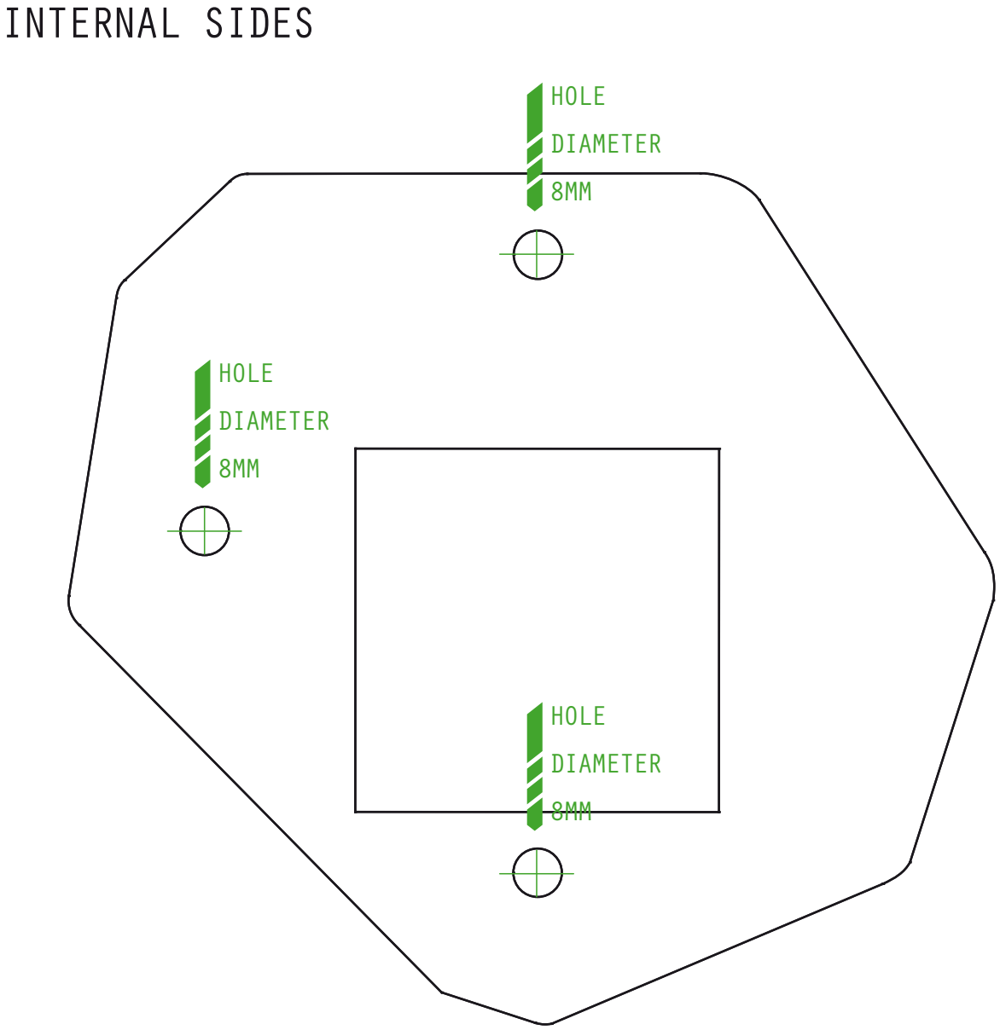
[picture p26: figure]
HOLE DIAMETER 8MM; INTERNAL SIDES

## PLAN 2

DEPENDING ON YOUR PERSONAL HEIGHT CHOOSE THE
SIZE RANGE THAT'S MORE SUITS YOU FROM THE DOTTED
OUTLINES

MORE THAN 170 CM

POSITIONING THE SLOTS FOR BELTS WERE YOU PREFER

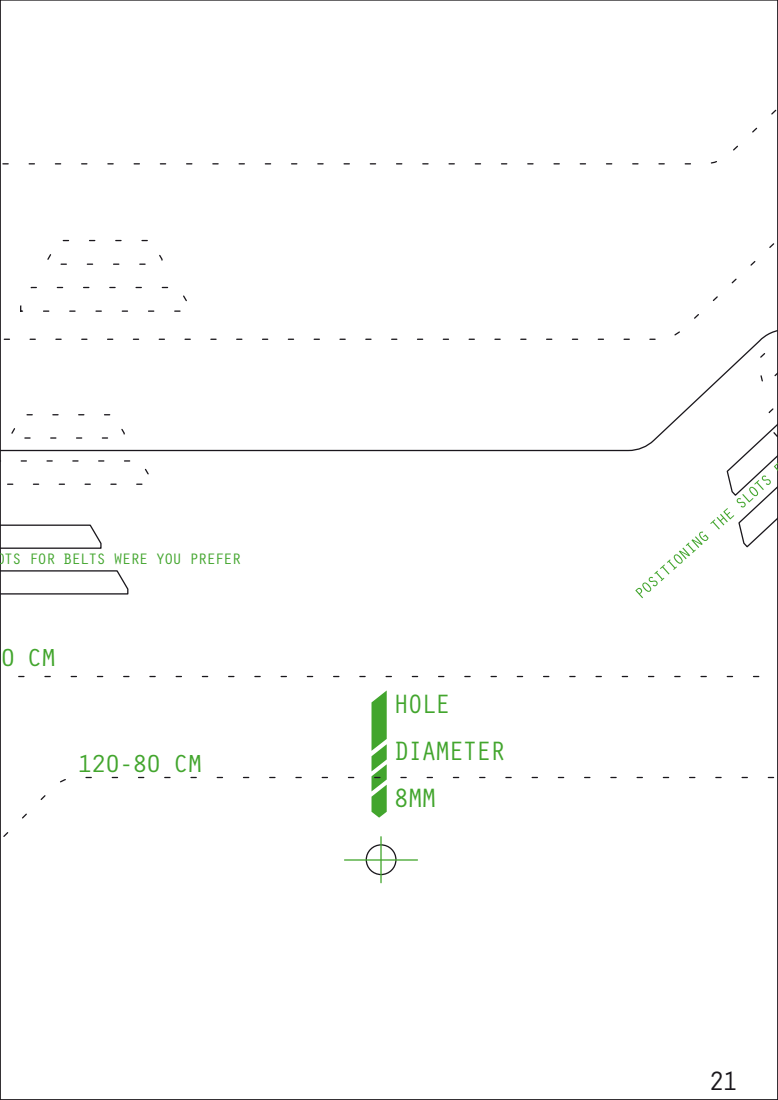
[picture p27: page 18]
HOLE DIAMETER 8MM

POSITIONING THE SLOTS FOR BELTS WERE YOU PREFER

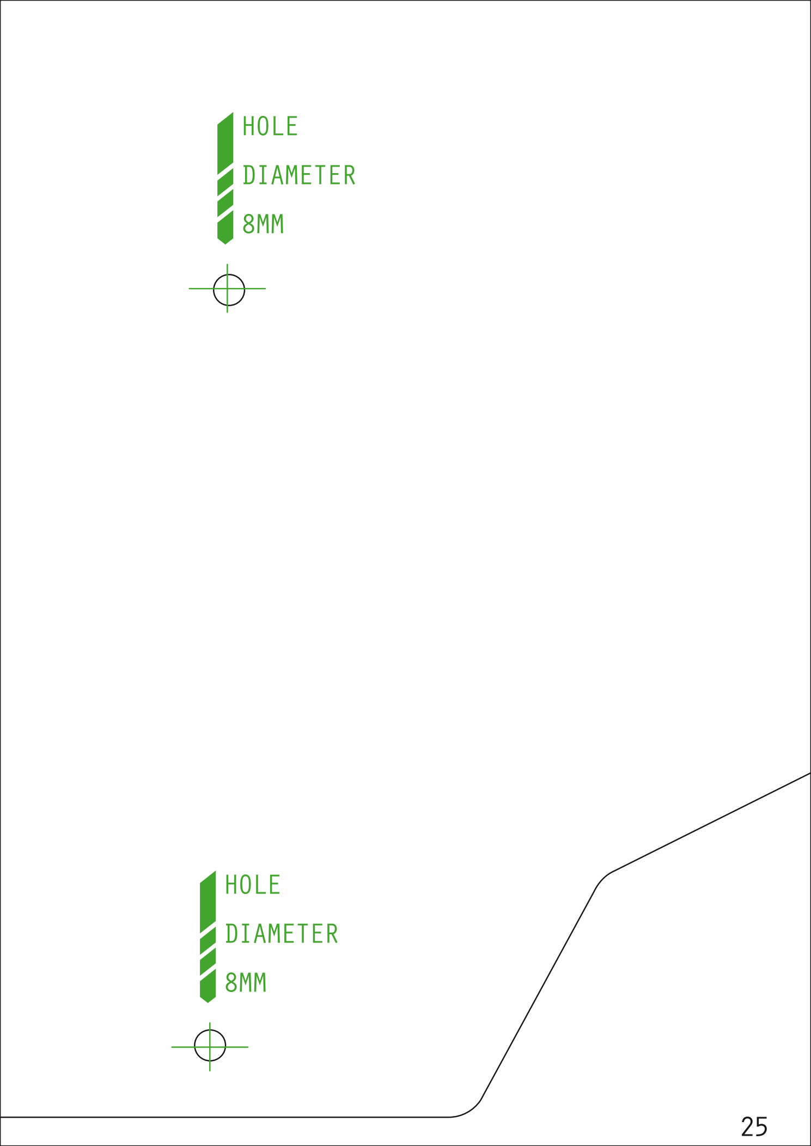
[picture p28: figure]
HOLE DIAMETER 8MM

## PLAN 6

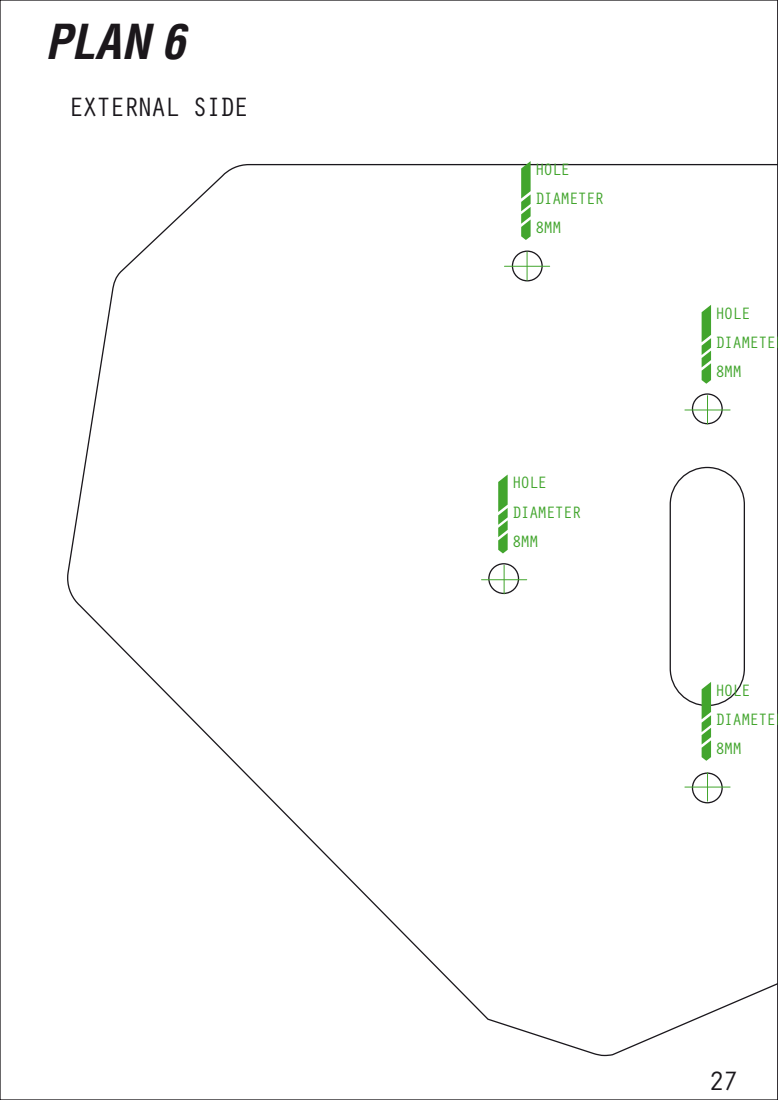
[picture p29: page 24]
EXTERNAL SIDE; HOLE DIAMETER 8MM

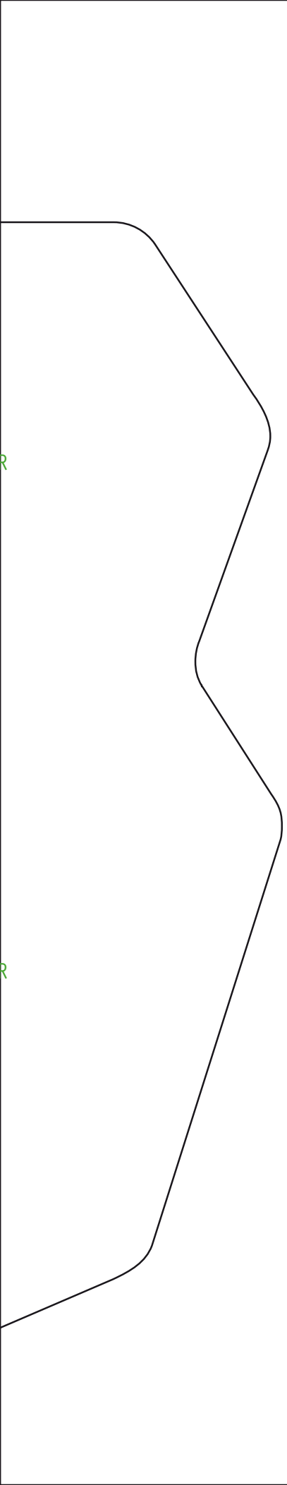
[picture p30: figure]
DIAMETER

INTERNAL SIDE

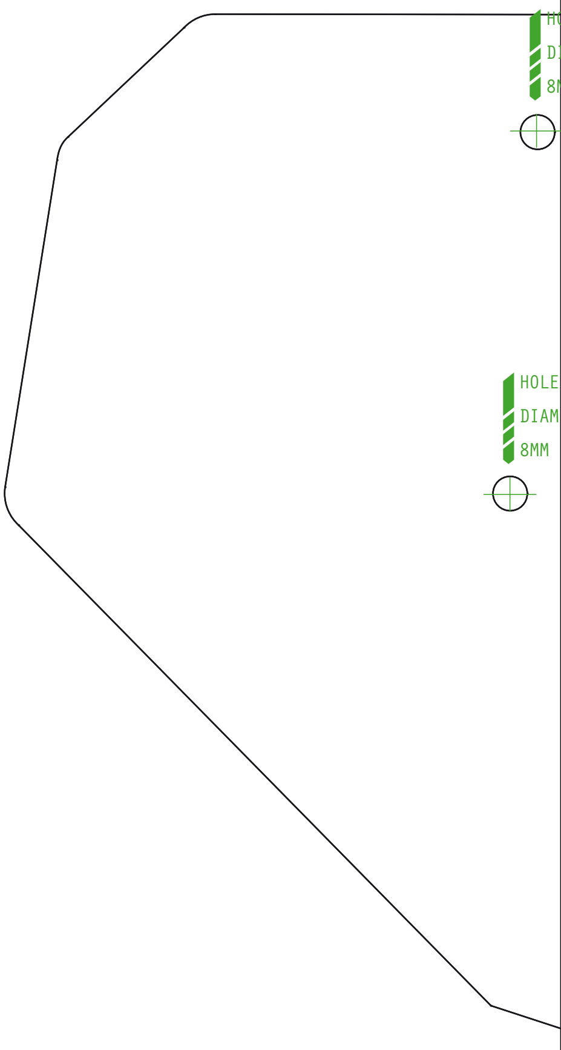
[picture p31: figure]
HOLE DIAMETER 8MM

INTERNAL SIDE

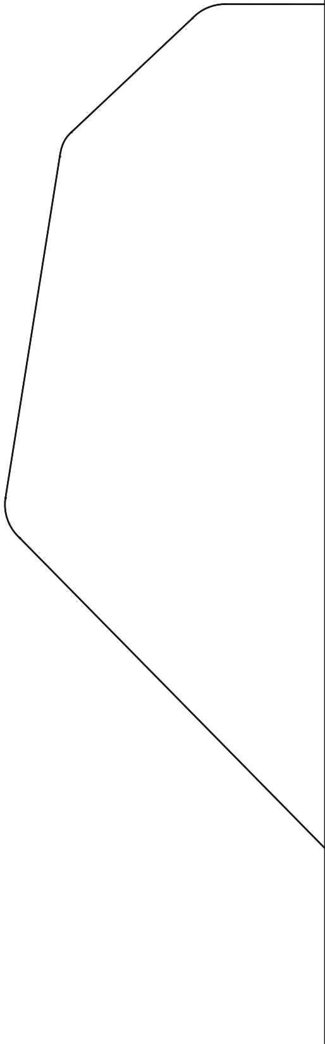
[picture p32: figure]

## PLAN 7

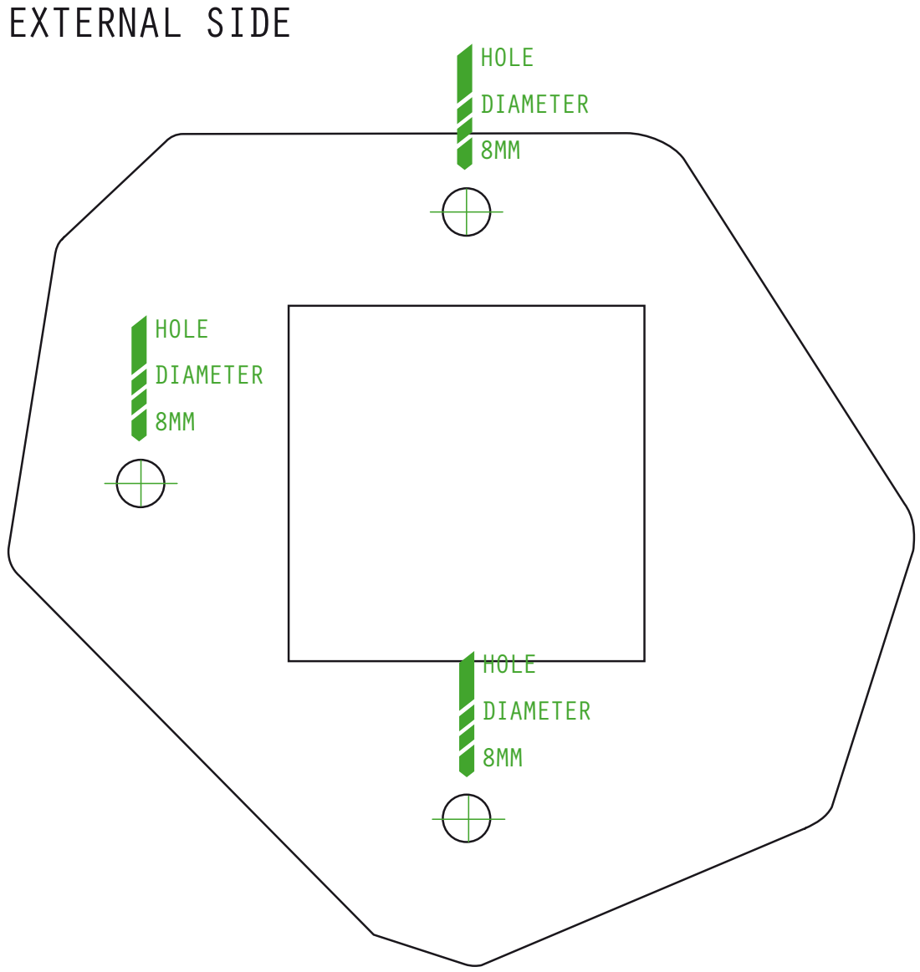
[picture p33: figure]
EXTERNAL SIDE; HOLE DIAMETER 8MM

## SEAT

SEAT
ITS WIDTH IS THE SAME OF YOUR A MEASURE AND ITS DEPTH IS THE SAME OF THE MEASURE B - 10CM. IF YOU WANT TO HAVE DIFFERENT SHAPER FOR EXTRA ERGONOMICS, CUT OFF SOME PART AND DESIGN YOUR REQUIRED SHAPES. THE DOTTED OUTLINE CAN BE AN EXAMPLE.

DEPTH: B-10CM

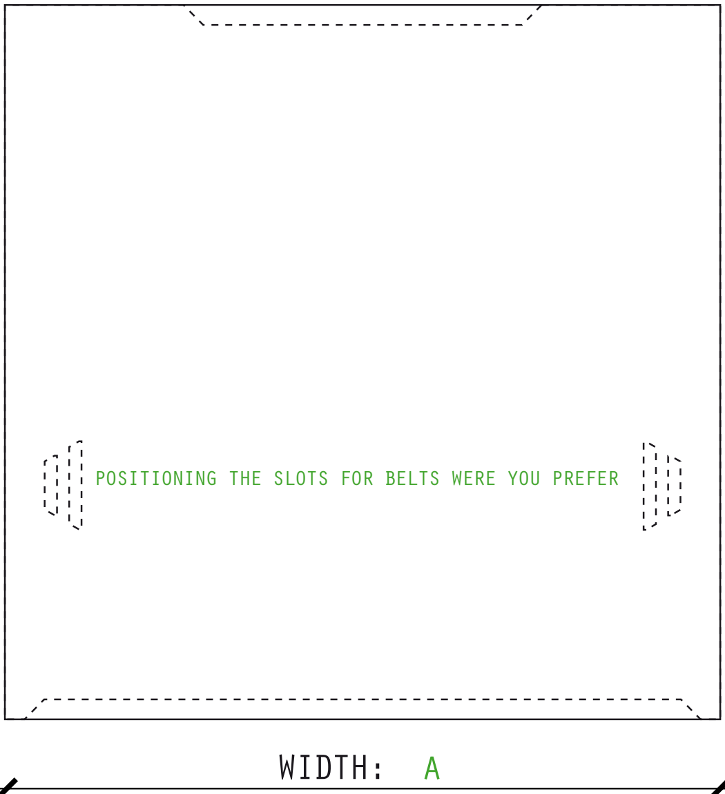
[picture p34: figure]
WIDTH: A

POSITIONING THE SLOTS FOR BELTS WERE YOU PREFER

## BACKREST

BACKREST
THE BACKREST WIDTH IS GIVEN BY THE A MEASURE, ITS HEIGHT FRO TH C MEASURE. FOR A BETTER COMFORT, YOU CAN CU OFF SOME PARTSAND DESIGN YOUR REQUIRED SHAPES.

HEIGHT:

C

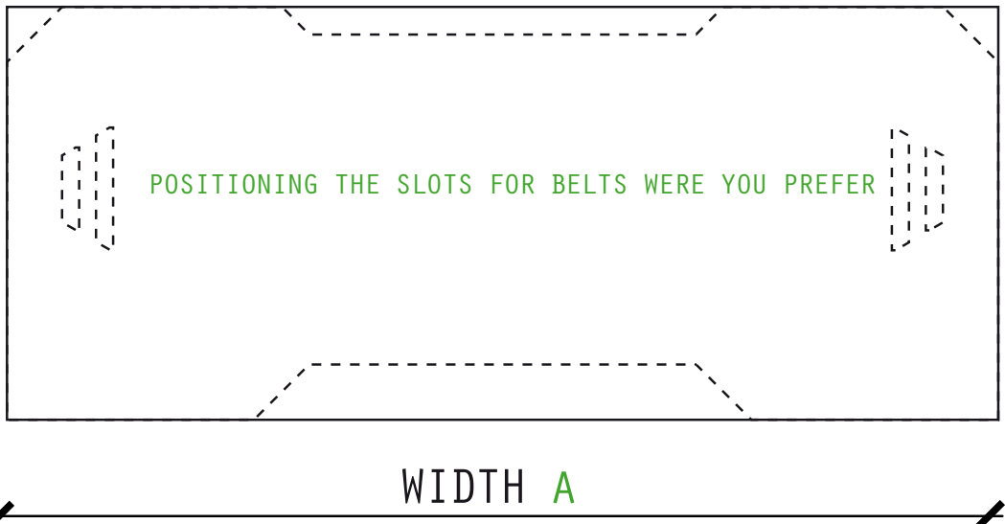
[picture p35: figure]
WIDTH A

POSITIONING THE SLOTS FOR BELTS WERE YOU PREFER

POGGIAPIEDI
THE WITH OF THIS PIECE IS YOUR A MEASURE, HIS HIGHT IS 20CM.

WIDTH: A

HIGHT: 20CM

## HORIZONTAL PANEL

## AXLE’S WEDGE

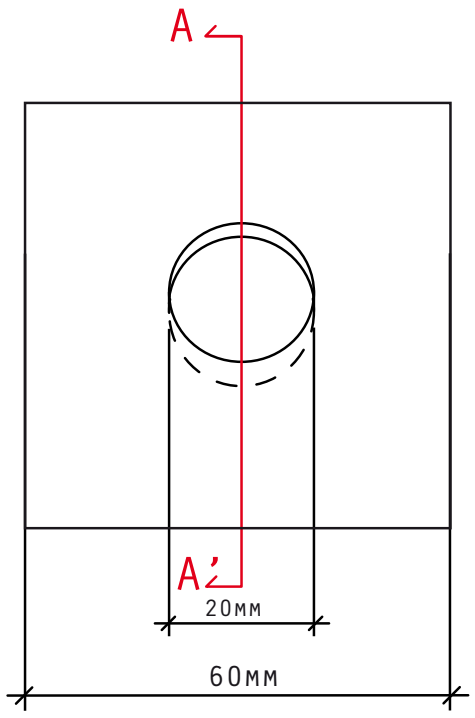
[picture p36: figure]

THE AXLE’S WEDGE ALLOW YOU TO HAVE THE DESIRED ANGLE OF THE WHEELS. YOU CAN CUT FROM WOOD OR 3D PRINT, BUT BE SHURE YOUR MATERIAL IS STRONG ENOUGH!
YOU CAN CHANGE THE ANGLE OF THE WEDGE FOR DIFFERENT WHEELS INCLINATION, OR IF YOU WANT VERTICAL WHEELS FOR EVERYDAY USE YOU CAN MAKE THE FACES OF THE WEDGE PARALLEL, WITH THE HOLE PERPENDICULAR AT THE FACES.

20mm

SECTION AA’

HUB’S FLANGE | FASE8

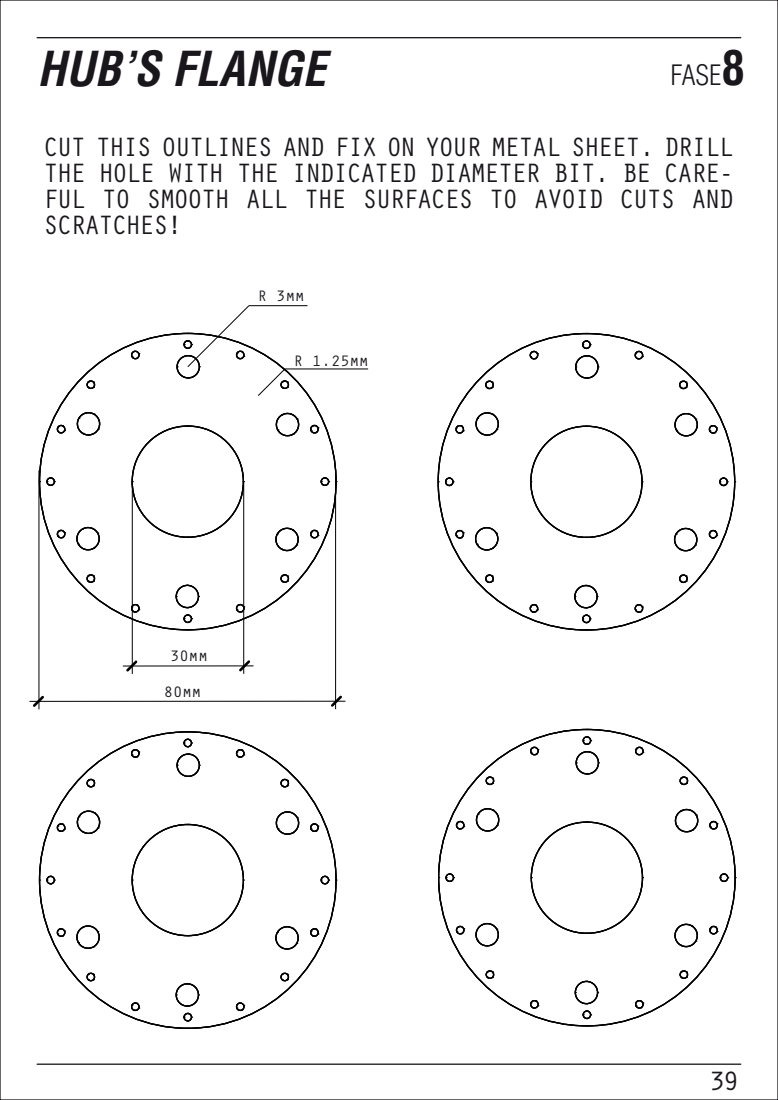
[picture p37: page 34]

CUT THIS OUTLINES AND FIX ON YOUR METAL SHEET. DRILL
THE HOLE WITH THE INDICATED DIAMETER BIT. BE CARE- FUL TO SMOOTH ALL THE SURFACES TO AVOID CUTS AND
SCRATCHES!

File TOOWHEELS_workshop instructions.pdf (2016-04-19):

# DO YOU WANT TO MAKE A WORKSHOP ABOUT TOOWHEELS?

Contact us, we will be happy to help you in setting-up the workshop for the replication of the project. We already cooperate with FabLabn Foundation and other foundations and research group all over the world, join us!

Here some info if you want to set up a workshop in your makerspace or fablab.

WORKSHOP DESCRIPTION

This workshop will teach you how to built your own wheelchair starting from the Toowheels project. Toowheels is the first DIY wheelchair, born from mixing design for all skills and maker’s world: www.toowheels.org.

During this workshop we explain you how to start in designing your wheelchair from the Toowheels user manual, customizing the project for your needs, making your own wheelchair using simple material and tools. At the end of the process you can use your chair, improving it as your fantasy want, and repairing easily broken parts!

NUMBER OF PEOPLE EACH INSTRUCTOR

It depend from a lot of thinks, bur more or less one instructor can support the building of 4 or 5 wheelchairs (better if people work in groups of 2/3 persons, especially if one of them as some disability).

ESTIMATED TIME

It’s possible to make a wheelchair in about 4 appointment of 3 hours each. I suggest to add one extra hour at the end of the workshop, so people can play and use together their new wheelchairs!

AGE REQUIRED

The process is not so difficult, so the workshop can be open from the age of 16 years old. But for the construction of the chair you have to cut some metal pipe and plywood sheet: the level of danger and difficulty depending on your kind of tools, so we suggest to have at least one adult each wheelchair you want to built.

LEVEL OF DIFFICULTY

The workshop can be open at beginners, because it’s made almost of simple operations.

HOW TO GET YOURSELF READY!

You don’t need any special skills to to this workshop, but if you have any basic understanding in cut and drill wood or metal parts it’s better. For the correct customization process of your wheelchair, you need to know how its works: we suggest you to be confidential with a wheelchair trying to use it, talking with people that use wheelchairs, looking for some images and videos of wheelchairs on internet in order to have an idea of this world.

TEAMS

For this workshop we suggest to let people work in team: at least 2 people each project and maximum 4. Take attention if one of the team has some disability and if needs help, eventually add some extra participant at the team!

WORK SPACE

For the workspace we suggest to have a 200 x 100 cm table each team for storage and assembling the wheelchair, eventually you can use the floor but it’s not so comfortable for people with disability. People can share one single working table, but It’s important to have some different tools in order to not slow down the work of the teams waiting’s. Use a projector for showing the slides of the workshop and we suggest you to have a blackboard to write and draw on. You don’t need chairs.

TOOLS NEEDED

You need:

- jigsaw wood cutter, at least one every 2 team but it’s better one saw each team;
- angle grinder, at least one every 2 teams;
- orbital sander, at least one every 2 teams, It is not required but it speeds up much of the work;
- sandpaper P40 and P220, more or less two 22 x 27 cm sheets for each type, each team. (use the sandpaper you want, remember you need to have a coarse and a fine finishing);
- drill, one each 2 teams with some different drill bits for wood and metal, especially 8mm, 10mm;
- spade bit of 16mm, one every 3/5 teams;
- laser machine, for cutting 10mm plywood, It is not required but it speeds up much of the work;
- dust mask, one each participant;
- working gloves, at least one pair each team;
- brush, at least one each team;

SAFETY CONSIDERATION

Be careful that people work in safety condition when they use electric tools or cutting tools. If they are beginners explain how to use and find some other instructor that can help you in mentoring the teams. Advise people using dust mask and safety gloves if they cut and sand wood or metal. We suggest to use sanding machines and paints at the open air.

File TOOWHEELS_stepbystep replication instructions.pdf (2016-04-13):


WWW.TOOWHEELS.ORG

TOOWHEELS IS A DIY WHEELCHAIR, YOU CAN BUILD USING SIMPLE
MATERIALS AND TOOLS: SOME PLYWOOD, SOME PIPES, SOME BICYCLE
YOU CAN CHANGE DIMENSION AND SIZE, AND IF YOU WANT YOU CAN
MAKE A CUSTOM WHEELCHAIR FOR ANY NEEDS YOU HAVE!
TOOWHEELS IS A PATENT PENDING PROJECT,

PARTS AND YOUR WHEELCHAIR IS READY!

RELEASED IN OPEN SOURCE VERSION (CC licence NON COMMERCIAL,
SHARE ALIKE) TO BE USEFULL FOR PEOPLE ALL OVER THE WORLD. MAKE IT FOR
YOUR FRIENDS, FOR PEOPLE OF YOUR CITY, MAKE IT IN A FABLAB OR A MA-

KERSPACE OR AT HOME!!
MAKE IT AND ENJOY!
FOLLOW US ON FB: TooWheels
SITE: WWW.TOOWHEELS.ORG
E-MAIL: ALESSIOFABRIZIOGIORGIO@GMAIL.COM


... ABOUT TOOWHEELS ...

# SEAT SEAT SUPPORT

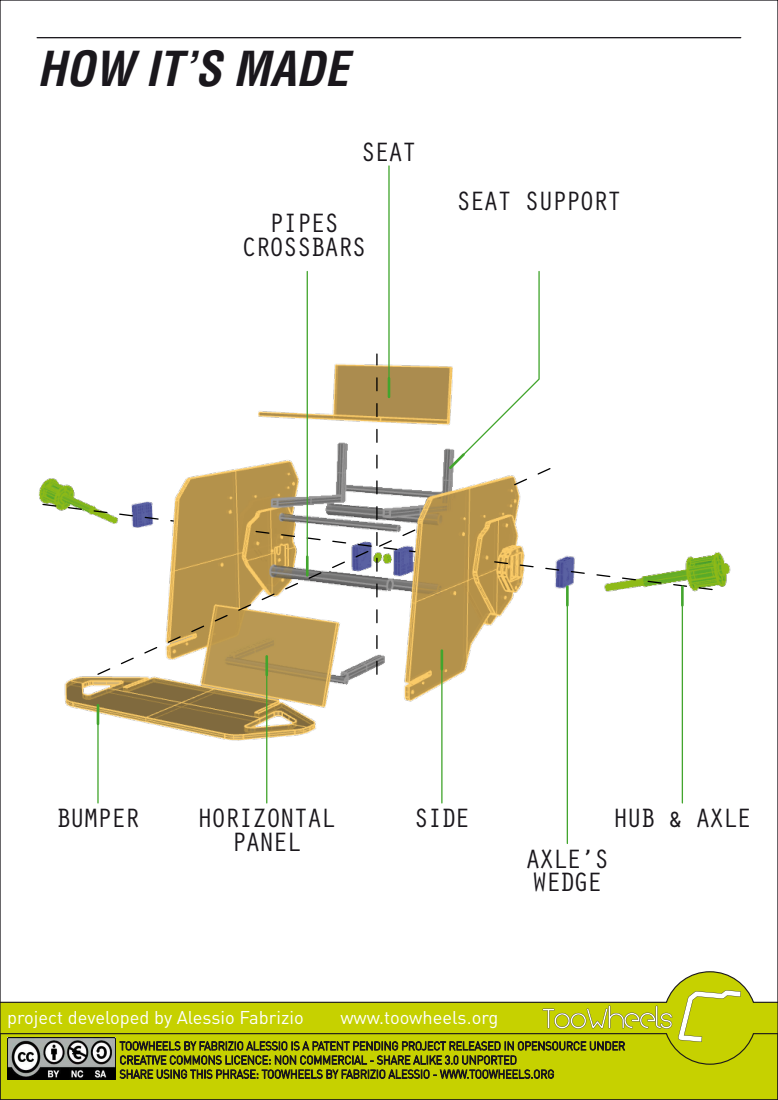
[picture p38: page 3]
HORIZONTAL PANEL; BUMPER; SIDE; AXLE’S WEDGE; HUB & AXLE; PIPES CROSSBARS; project developed by Alessio Fabrizio; www.toowheels.org

HOW IT’S MADE

TOOWHEELS BY FABRIZIO ALESSIO IS A PATENT PENDING PROJECT RELEASED IN OPENSOURCE UNDER
CREATIVE COMMONS LICENCE: NON COMMERCIAL - SHARE ALIKE 3.0 UNPORTED
SHARE USING THIS PHRASE: TOOWHEELS BY FABRIZIO ALESSIO - WWW.TOOWHEELS.ORG

# do it yourself! follow this steps!

STEP 1 1.1 - print the TW project sheets 1.2 - assembling the sheets using scotch tape 1.3 - customize the TW project’s dimention and shapes 1.4 - cut the paper pattern and put on the plywood sheets 1.5 - sign up the outlines and holes with a pencil 1.6 - start cutting and drilling parts 1.7 - sand and smooth plywood

# STEP 2 2.1 - cut the pipes 2.2 - glue the plywood parts 2.3 - cut the hub’s flange from the metal sheet 2.4 - cut and hole the wedge for the axle

# STEP 3 3.1 - cut foam foil 3.2 - paint plywood 3.3 - assemble the hub 3.4 - assemble the wheel spokes

# STEP 4 4.1 - assemble and fix all the part 4.2 - cut the excess part of the threaded rods 4.3 - fix foam 4.4 - let’s play!

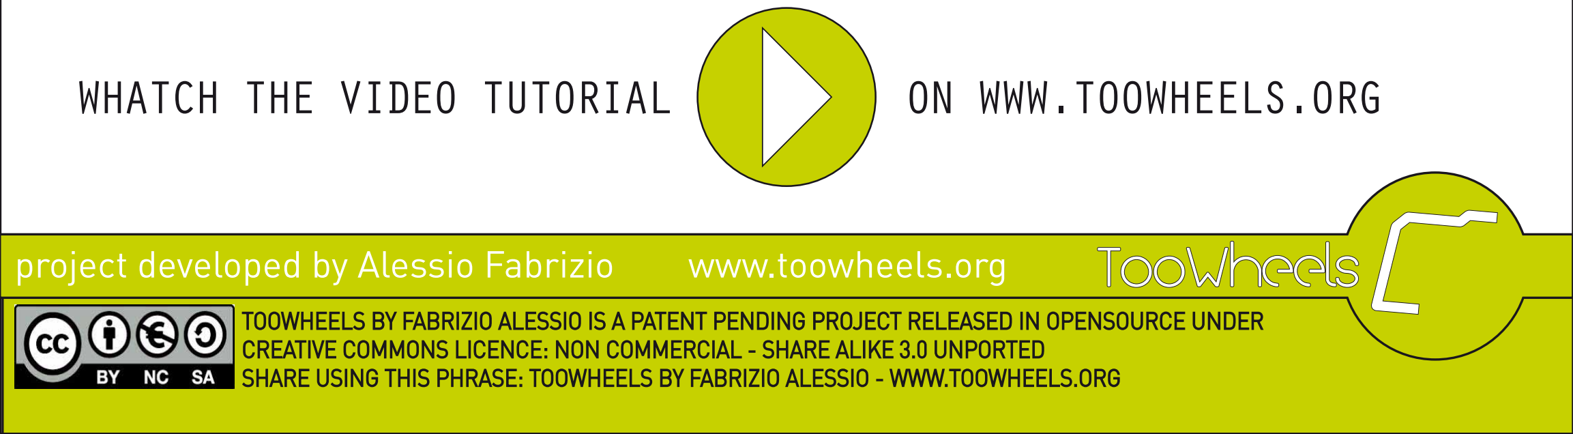
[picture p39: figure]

WHATCH THE VIDEO TUTORIAL | ON WWW.TOOWHEELS.ORG

# print the TW project sheets

# PRINT THE PROJECT MANUAL WITH ISO A4 PAPER. PRINT AT

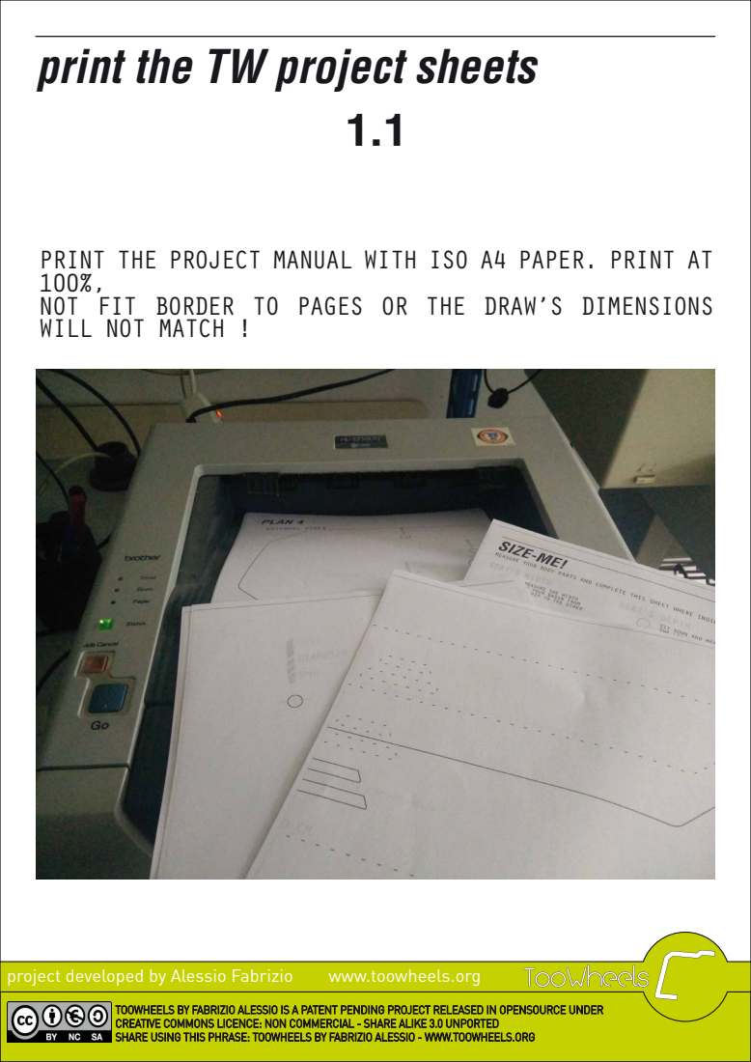
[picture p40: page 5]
project developed by Alessio Fabrizio; www.toowheels.org

NOT FIT BORDER TO PAGES OR THE DRAW’S DIMENSIONS
WILL NOT MATCH !

# assembling the sheets

USE SCOTCH TAPE TO FIX THE PLANS SHEETS TOGHETHER,

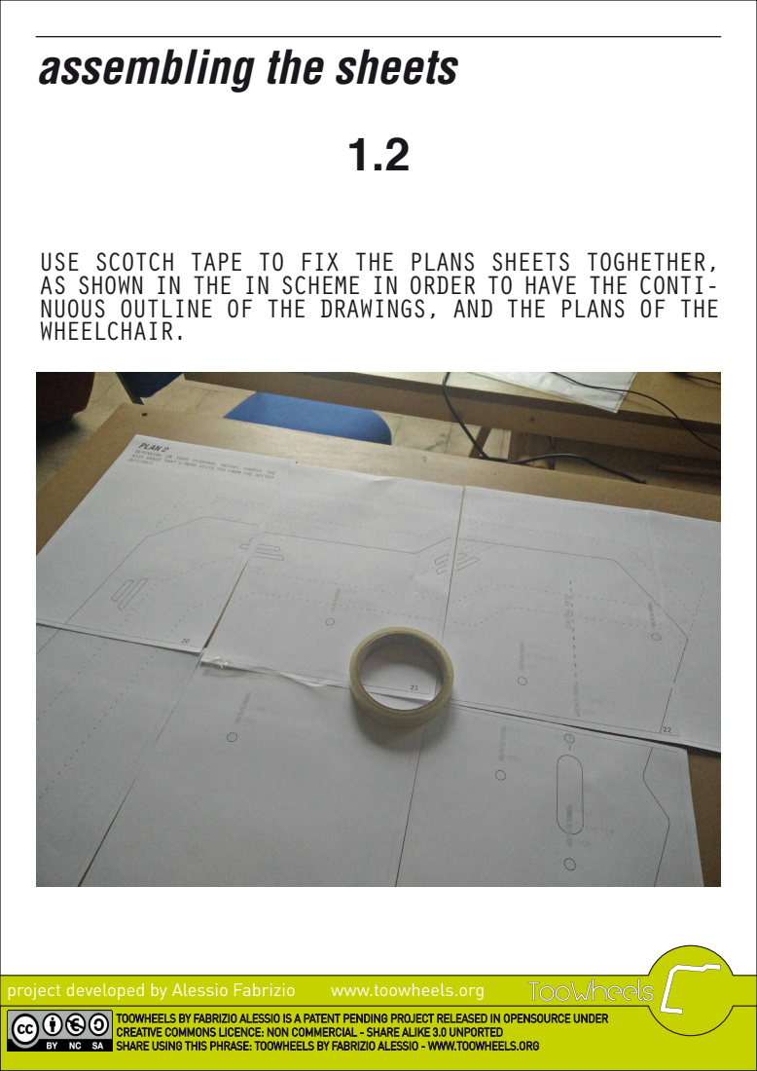
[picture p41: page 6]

AS SHOWN IN THE IN SCHEME IN ORDER TO HAVE THE CONTI- NUOUS OUTLINE OF THE DRAWINGS, AND THE PLANS OF THE
WHEELCHAIR.

# customize your TW project’s

1.3

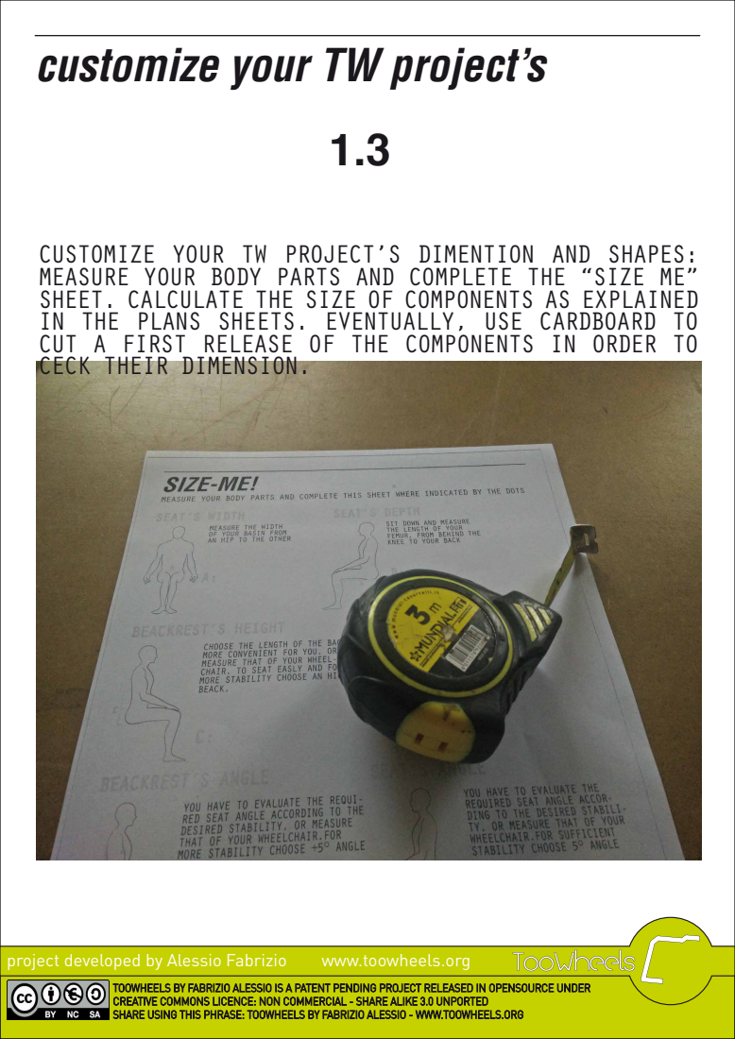
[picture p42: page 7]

CUSTOMIZE YOUR TW PROJECT’S DIMENTION AND SHAPES:
MEASURE YOUR BODY PARTS AND COMPLETE THE “SIZE ME”
SHEET. CALCULATE THE SIZE OF COMPONENTS AS EXPLAINED
IN THE PLANS SHEETS. EVENTUALLY, USE CARDBOARD TO
CUT A FIRST RELEASE OF THE COMPONENTS IN ORDER TO
CECK THEIR DIMENSION.

# cut the paper plans

CUT THE PAPER PATTERN AND PUT ON THE PLYWOOD SHEETS,

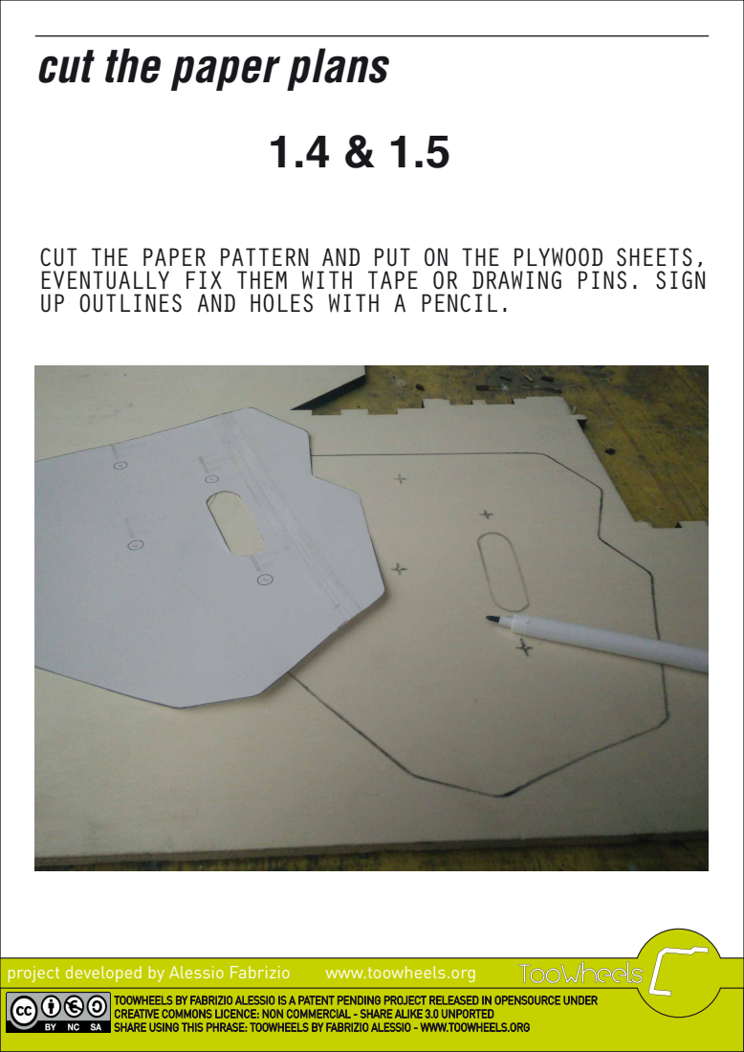
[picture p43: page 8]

EVENTUALLY FIX THEM WITH TAPE OR DRAWING PINS. SIGN
UP OUTLINES AND HOLES WITH A PENCIL.

# cut the plywood sheets

# START CUTTING AND DRILLING ALL THE PARTS. SMOOTH ALL

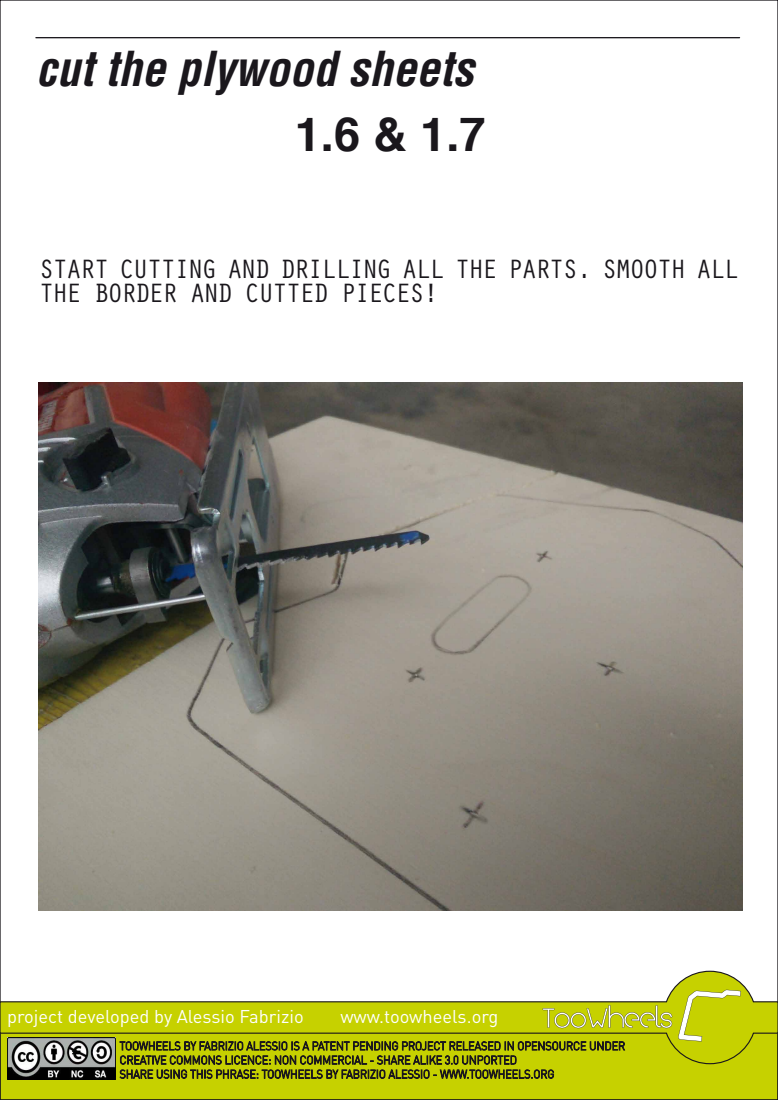
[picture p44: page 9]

THE BORDER AND CUTTED PIECES!

# cut the pipes

# CUT THE ALUMINIUM PIPES USING PIPE-CUTTER OR AN

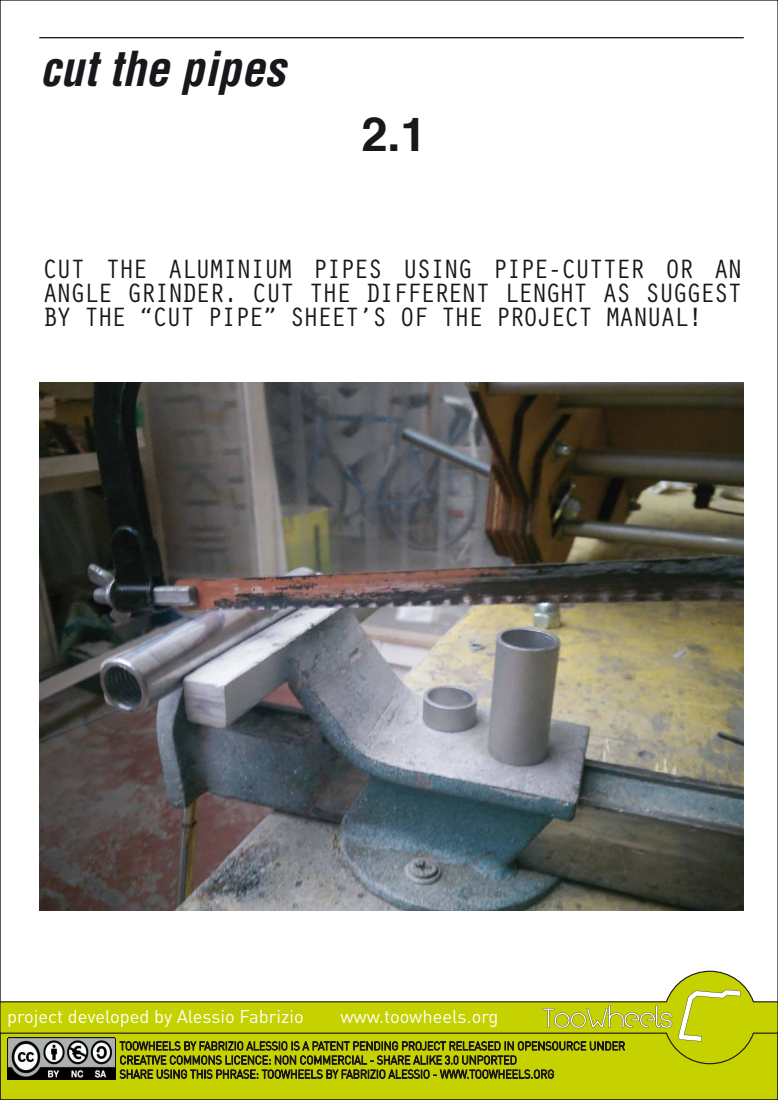
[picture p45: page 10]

ANGLE GRINDER. CUT THE DIFFERENT LENGHT AS SUGGEST
BY THE “CUT PIPE” SHEET’S OF THE PROJECT MANUAL!

# glue the plywood parts

GLUE ALL THE PART AS SHOWN IN THE SCHEME, BE CARE- FULL IN INTERNAL AND EXTERNAL PANELS AND SIDES!

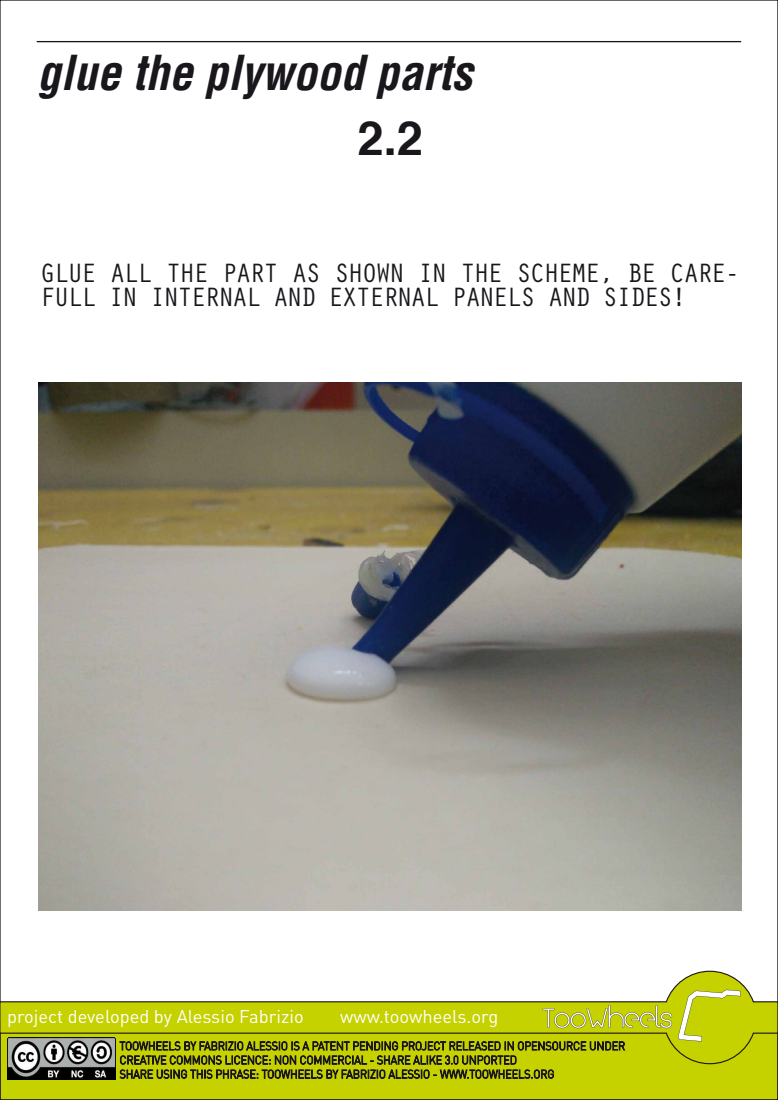
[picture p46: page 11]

# cut the hub’s ange

# FROM YOUR METAL SHEET, CUT THE FLANGE USING THE


PLANS ON THE MANUAL: CUT THE PAPER OUTLINE, FIX ON
THE METAL SHEET AND MARK THE OUTLINE AND HOLES.
DRILL AND CUT, AND REMEMBER TO SMOOTH ALL THE
SURFACE!YOU HAVE TO BE SURE TO MAKE IN THE FLANGES
THE SAME NUMBER OF HOLES YOU NEED FOR THE WHEELS
SPOKES!

# cut and hole the wedge for the axle

# FROM YOUR WOOD BEAM CUT AN ANGULATED SLICE. THE


ANGLE YOU CHOOSE BECOME THE ANGLE FOR YOUR WHEELS
DISHING.

# cut foam foil

# FIND A FOAM SHEET, AND CUT SOME PIECES TO COVER SEAT


AND BACKREST, AND IF YOU WANT ALSO THE LATERAL
SIDES.

# paint plywood

# FOR AN EXTRA FINISHING AND DURATION, PAINT YOU


WOODEN PARTS TO PROTECT THEM FROM WATER AND HUMIDI- TY.

# assemble the hub

# FOLLOW THE HUB’S PROJECT SCHEME TO ASSEMBLING THE


BEARING WITH ALL THE PIPES AND THE HUB’S FLANGES.

# assemble the wheels spokes

# ASSEMBLING YOUR HUB WITH THE BICYCLE WHEELS. IT’S


NOT EASY TO FIX THE SPOKES IN THE RIGHT POSITION,
ASK TO SOMEONE EXPERT IN BICYCLE’S REPAIR OR CHECK
SOME TUTORIAL ON THE WEB!

# assemble and x all the parts!

# ASSEMBLE ALL THE PLYWOOD LAYER AND FIX THE THREADED


RODS USING NUTS AND WASHERS. BE CAREFUL TO SCREW
TIGHT ALL PARTS!

# cut the excess part of threaded rods

CUT THE EXCESS PART OF THE THREADED RODS.


# x foam

# FIX THE FOAM USING GLUE OR SOME TAPE. IF YOU NEED


TOU CAN FIX SOME BELTS AT THE WHEELCHAIR FOR A MORE
CONFORTABLE USE.

# let’s play!

# ENJOY YOUR TOOWHEELS!


IMPROVE YOUR WHEELCHAIR ADDING STUFF AND DEVELOP
YOUR OWN SET UP, EVEN CREATING WHEELCHAIR FOR DIFFE- RENT ACTIVITY!
